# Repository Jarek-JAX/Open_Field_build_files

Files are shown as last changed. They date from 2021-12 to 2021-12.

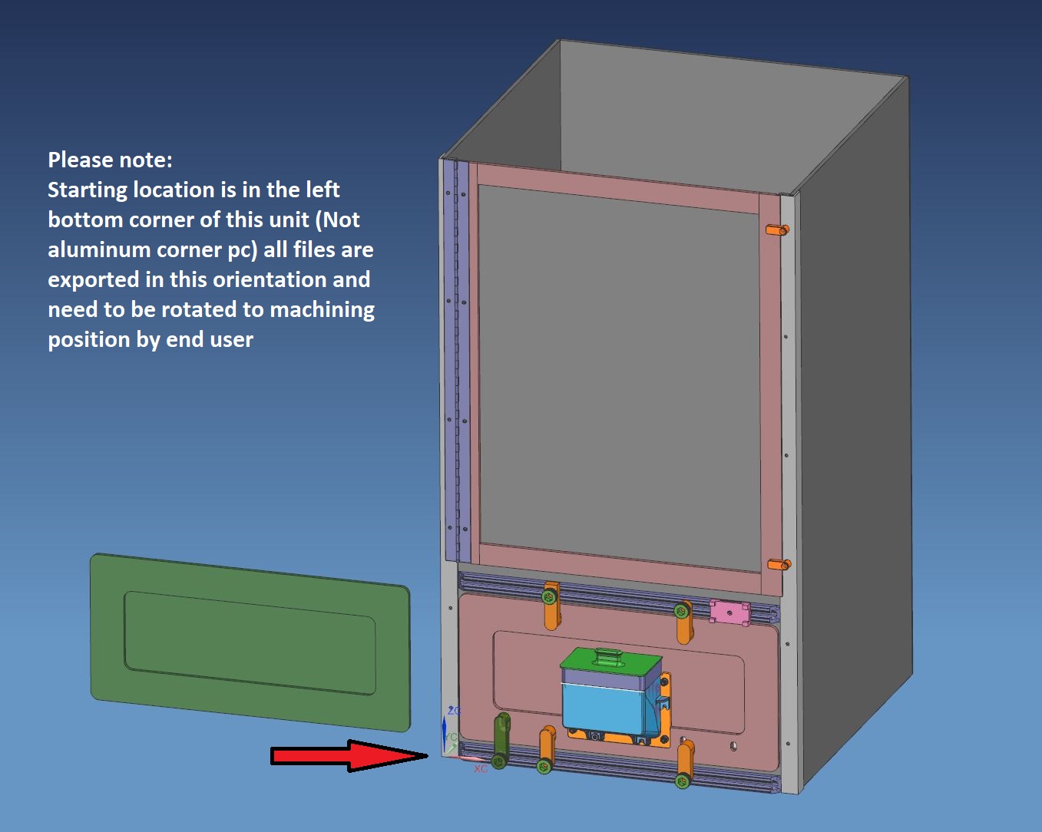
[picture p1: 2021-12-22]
02_Starting_location_and_orientation.JPG

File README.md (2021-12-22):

# Open_Field_build_files
All files listed and posted are created in US inch format and can be easily converted using FreeCad or similar open source CAD program.
All .step files are 3D CAD models needed to create CNC programs for cutting, and size verifications. Please follow Files list for quantities needed and Assembly instructions
Aluminum food grade is also shown as Drafting in pdf for outsourcing machining throug for eg. www.hubs.com

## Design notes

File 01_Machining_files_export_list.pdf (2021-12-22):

All Files are exported in .STEP203 Format | All Dimmensions are in US Inch

links:
Name | Material | Required
1 Floor | EXP PVC - White | 1 | *** EXP PVC White (https://www.curbellplastics.com/Shop-Materials/Product/Sintra-Expanded-PVC-Sheet/W01-06173/SINTRA-Expanded-PVC-Sheet-SINTRA-VERS-(formerly-e-pvc-)-Bright-Whit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)
2 Back_Wall | EXP PVC - Light Gray | 1
3 Side_Walls | EXP PVC - Light Gray | 2 | **** EXP PVC Light Gray (https://www.curbellplastics.com/Shop-Materials/Product/Sintra-Expanded-PVC-Sheet/W01-01036/SINTRA-Expanded-PVC-Sheet-SINTRA-Light-Gray-(6-mm-x-48-in-x-96-in)-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)
4 Front_Wall | EXP PVC - Light Gray | 1
5 Upper_Door | EXP PVC - Light Gray | 1 | Aluminum_Rail_Cut (https://www.mcmaster.com/47065T68-47065T681/)
6 Door_Frame_Long_1 | EXP PVC - Light Gray | 1
7 Door_Frame_Long_2 | EXP PVC - Light Gray | 1 | Derlin (https://www.mcmaster.com/8573K13/)
8 Door_Frame_Short | EXP PVC - Light Gray | 1
9 Front_Panel_Food_1 | EXP PVC - Light Gray | 1 | Aluminum_Corner (https://www.mcmaster.com/88805K77-88805K774/)
10 Front_Panel_Food_2 | EXP PVC - Light Gray | 1
11 Front_Panel_Blank_1 | EXP PVC - Light Gray | 1 | Piano_Hinge (https://www.mcmaster.com/1658A15-1658A4/)
12 Front_Panel_Blank_2 | EXP PVC - Light Gray | 1
13 Food_Grade | Aluminum | 1
14 Aluminum_Rail_Cut | Aluminum | 2
15 Light_ring_square | Derlin (Or simmilar) | 1
16 Aluminum_Corner | Aluminm | 2
17 Piano_Hinge | Stainless_Steel | 1

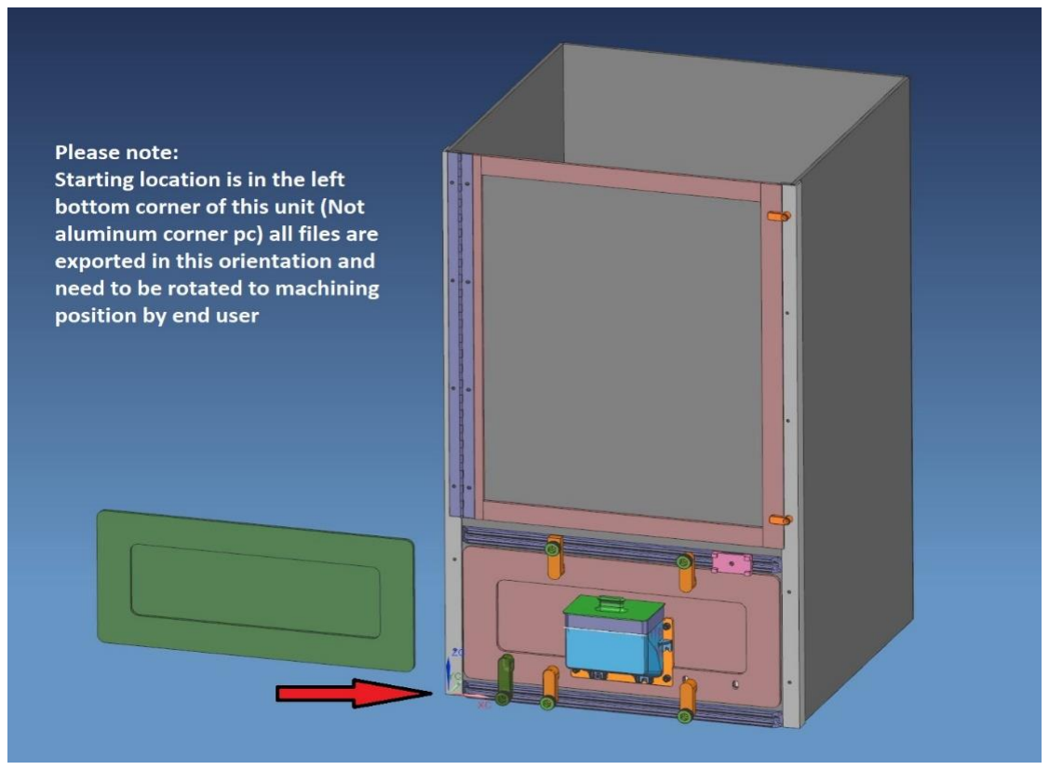
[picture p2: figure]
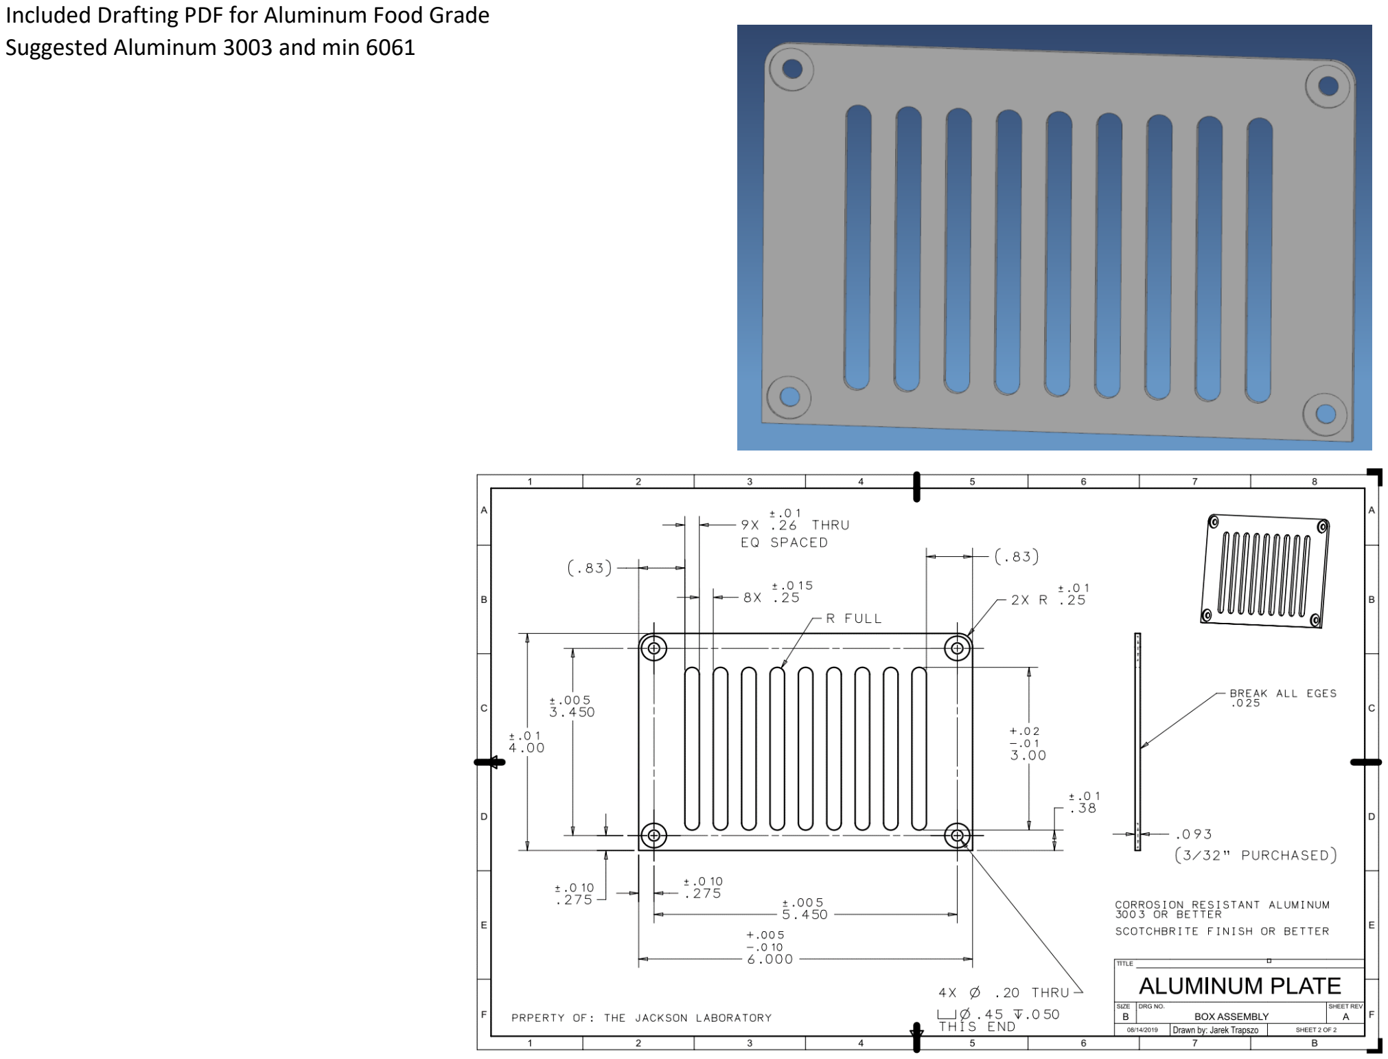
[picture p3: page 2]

Included Drafting PDF for Aluminum Food Grade Suggested Aluminum 3003 and min 6061

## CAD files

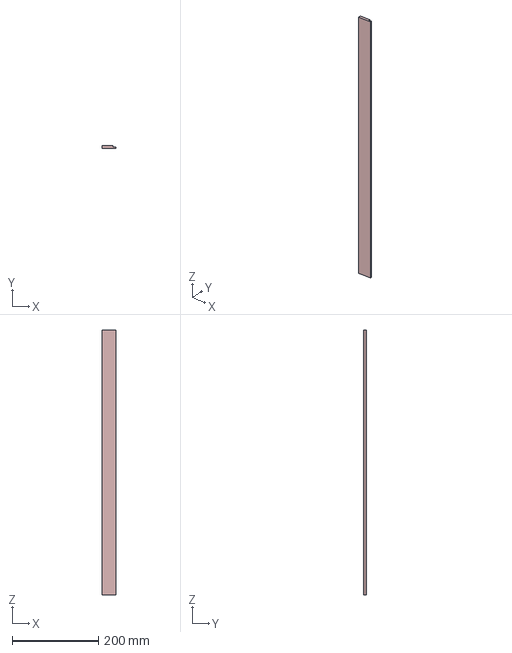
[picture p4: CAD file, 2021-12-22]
Door_frame_Long_1.stp
31.7 x 6.35 x 613.4 mm

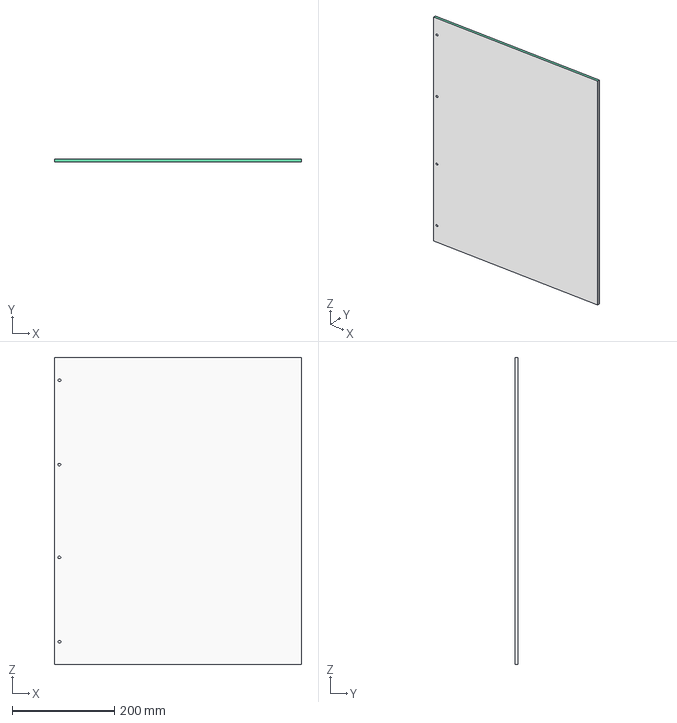
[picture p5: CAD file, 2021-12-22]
Upper_Door.stp
483.4 x 6.35 x 600.7 mm

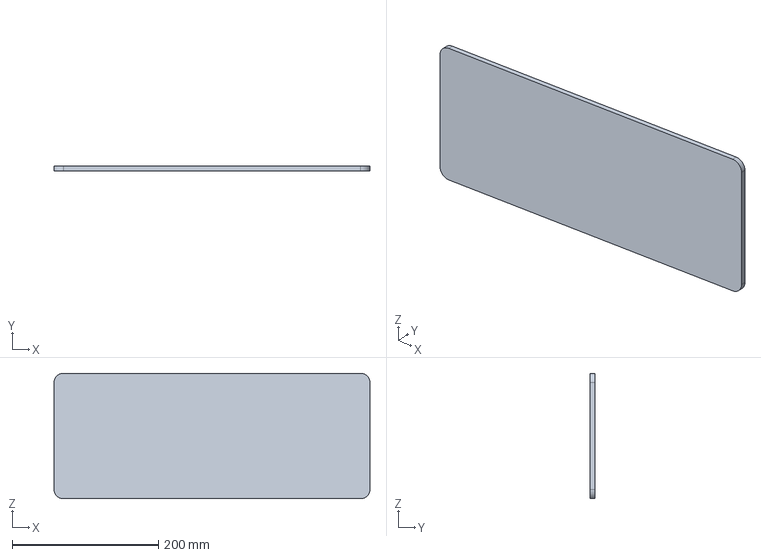
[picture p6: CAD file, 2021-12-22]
Front_Panel_Blank_1.stp
431.8 x 6.35 x 171.5 mm

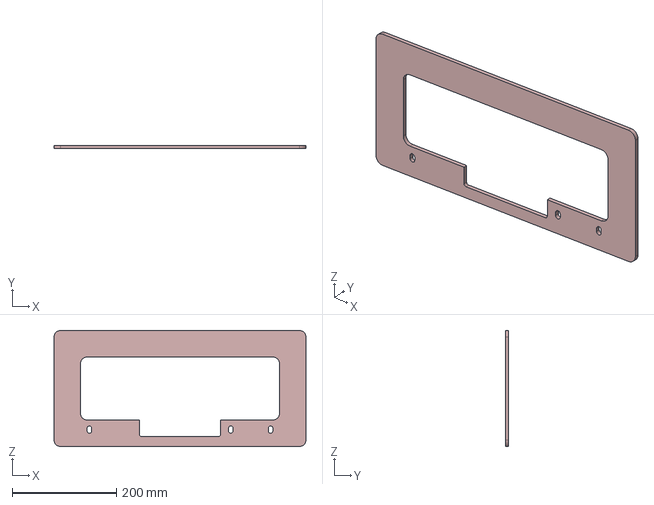
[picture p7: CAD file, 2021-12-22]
Front_Panel_Food_2.stp
482.6 x 6.35 x 222.2 mm

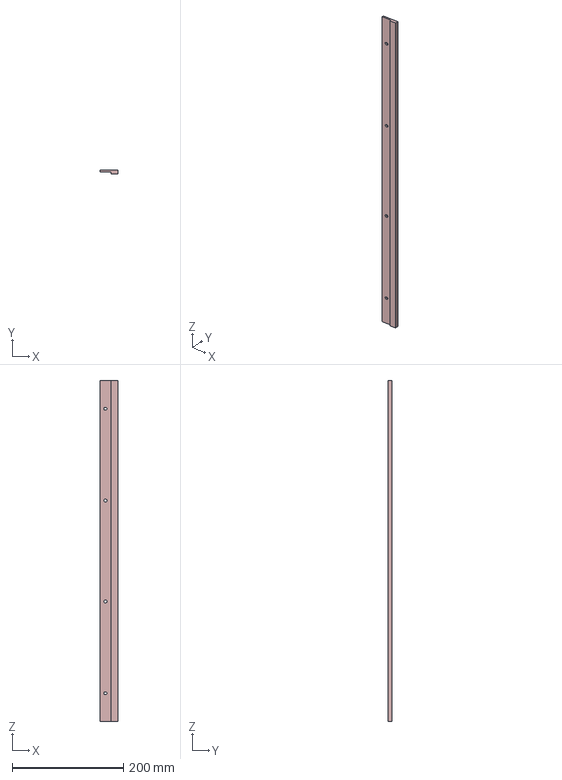
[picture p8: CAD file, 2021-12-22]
Door_frame_Long_2.stp
31.8 x 6.35 x 613.4 mm

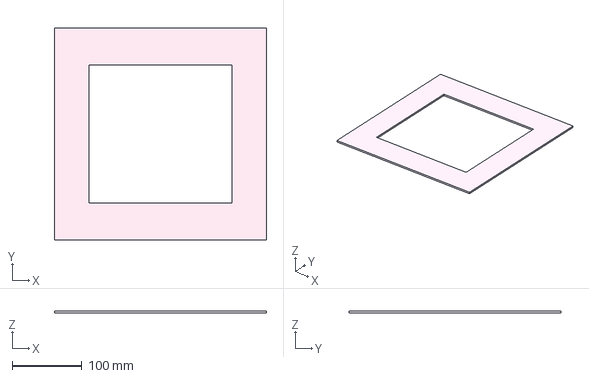
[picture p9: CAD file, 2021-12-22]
Light_ring_square.stp
304.8 x 304.8 x 3.18 mm

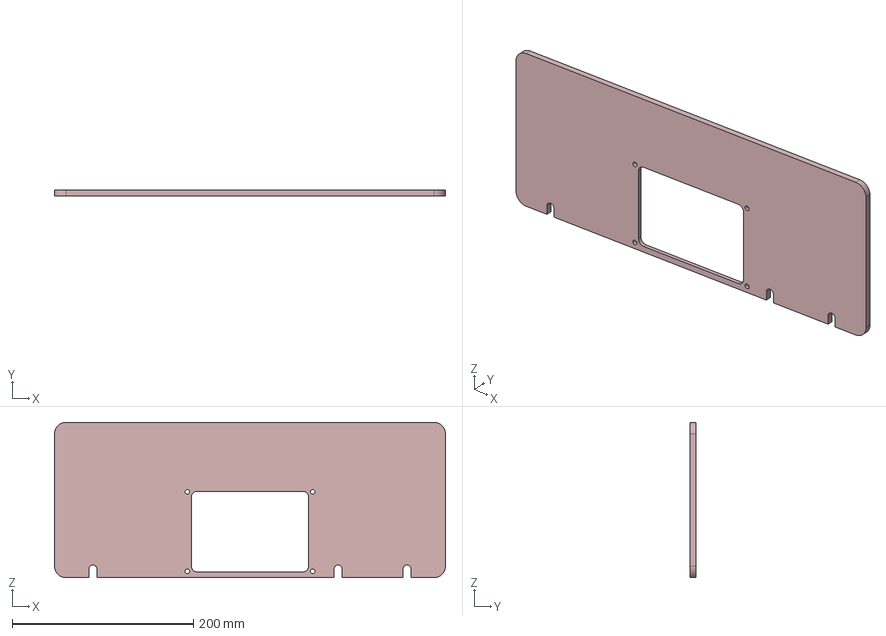
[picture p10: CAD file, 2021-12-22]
Front_Panel_Food_1.stp
431.8 x 6.35 x 171.5 mm

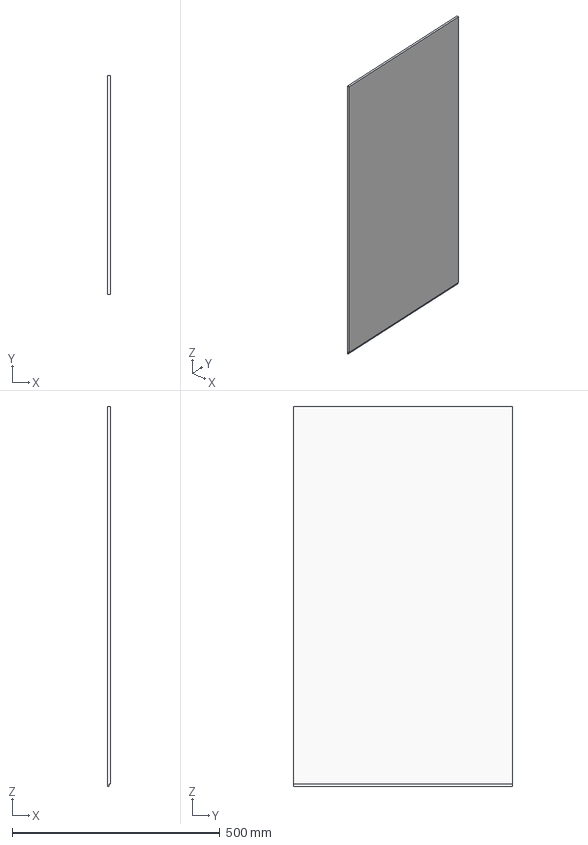
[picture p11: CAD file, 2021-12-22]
Side_Walls.stp
6.35 x 527.1 x 914.4 mm

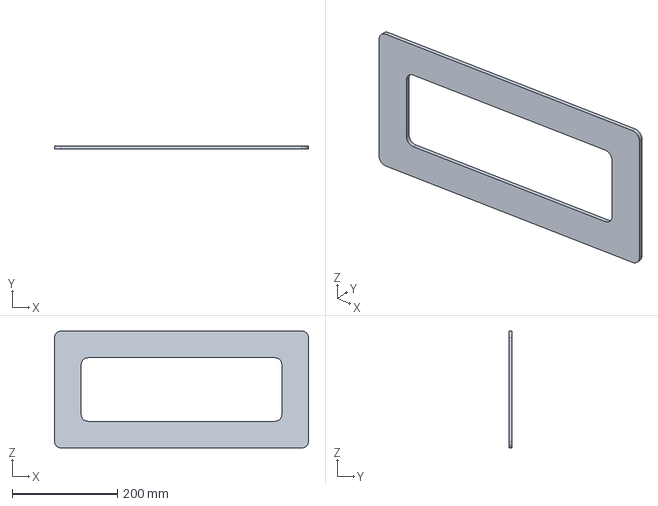
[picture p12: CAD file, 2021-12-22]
Front_Panel_Blank_2.stp
482.6 x 6.35 x 222.2 mm

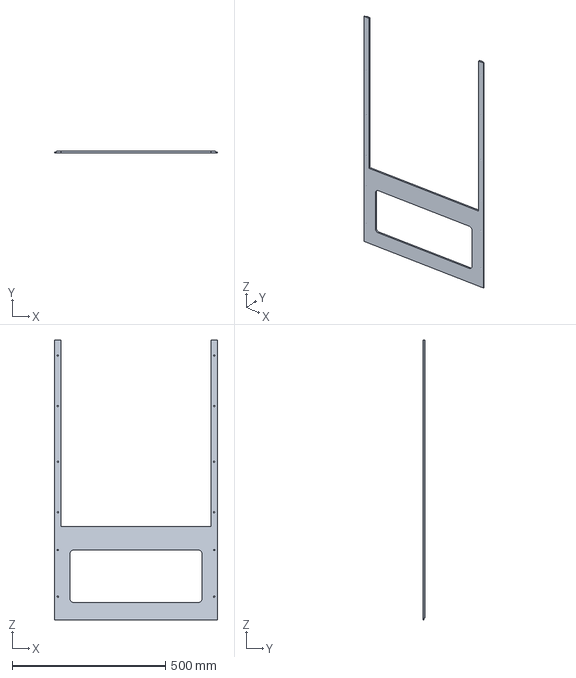
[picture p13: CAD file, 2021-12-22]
Front_wall.stp
533.4 x 6.35 x 914.4 mm

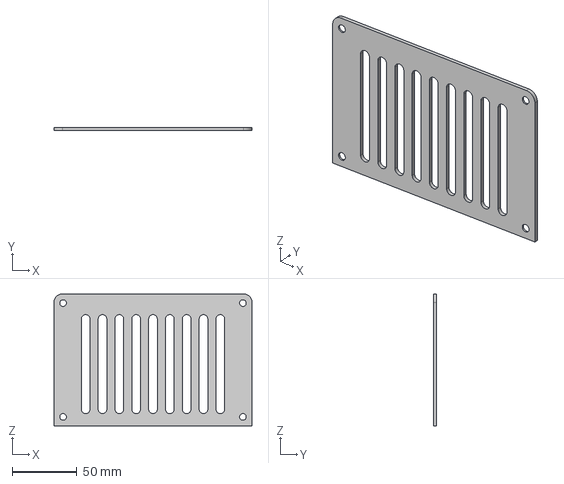
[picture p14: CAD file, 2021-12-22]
Food_Grade.stp
152.4 x 2.36 x 101.6 mm

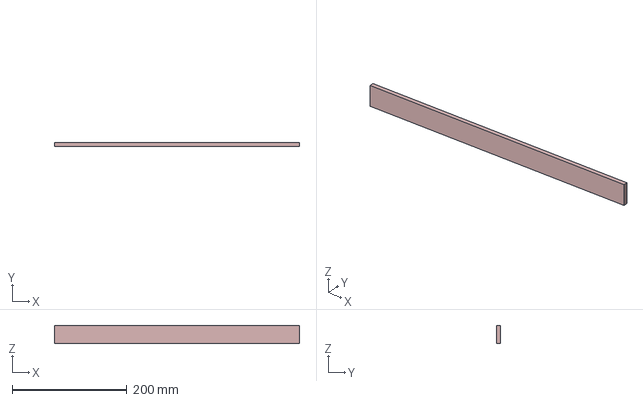
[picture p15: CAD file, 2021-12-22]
Door_frame_Short.stp
426.7 x 6.35 x 31.8 mm

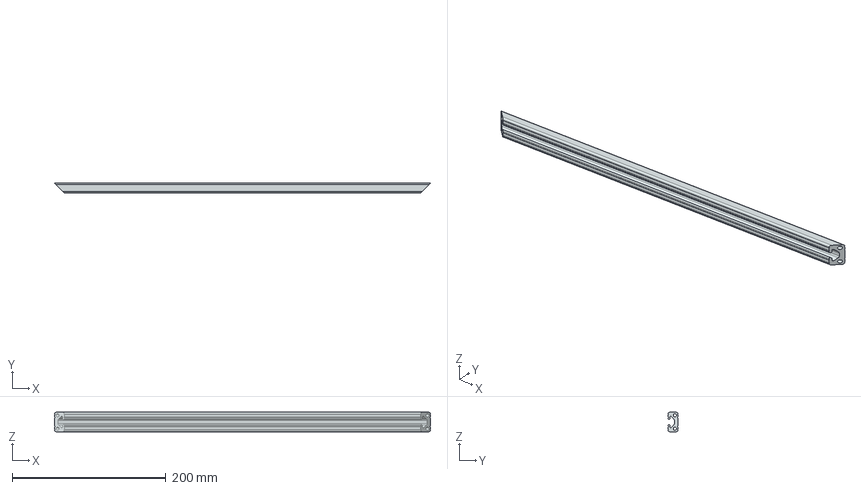
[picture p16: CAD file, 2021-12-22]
Alluminum_rail_cut.stp
488.7 x 12.7 x 25.4 mm

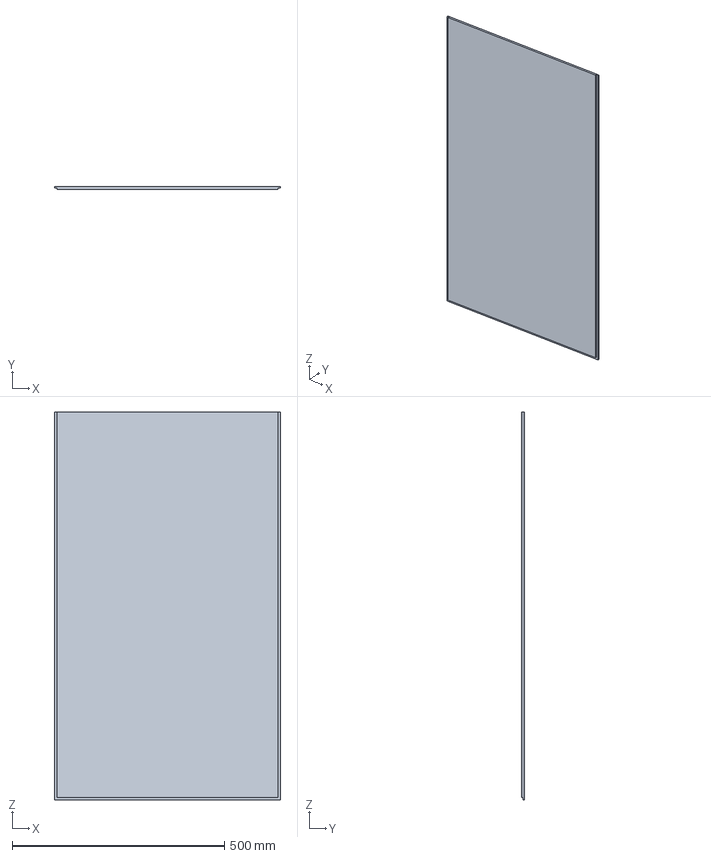
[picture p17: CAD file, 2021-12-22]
Back_Wall.stp
533.4 x 6.35 x 914.4 mm

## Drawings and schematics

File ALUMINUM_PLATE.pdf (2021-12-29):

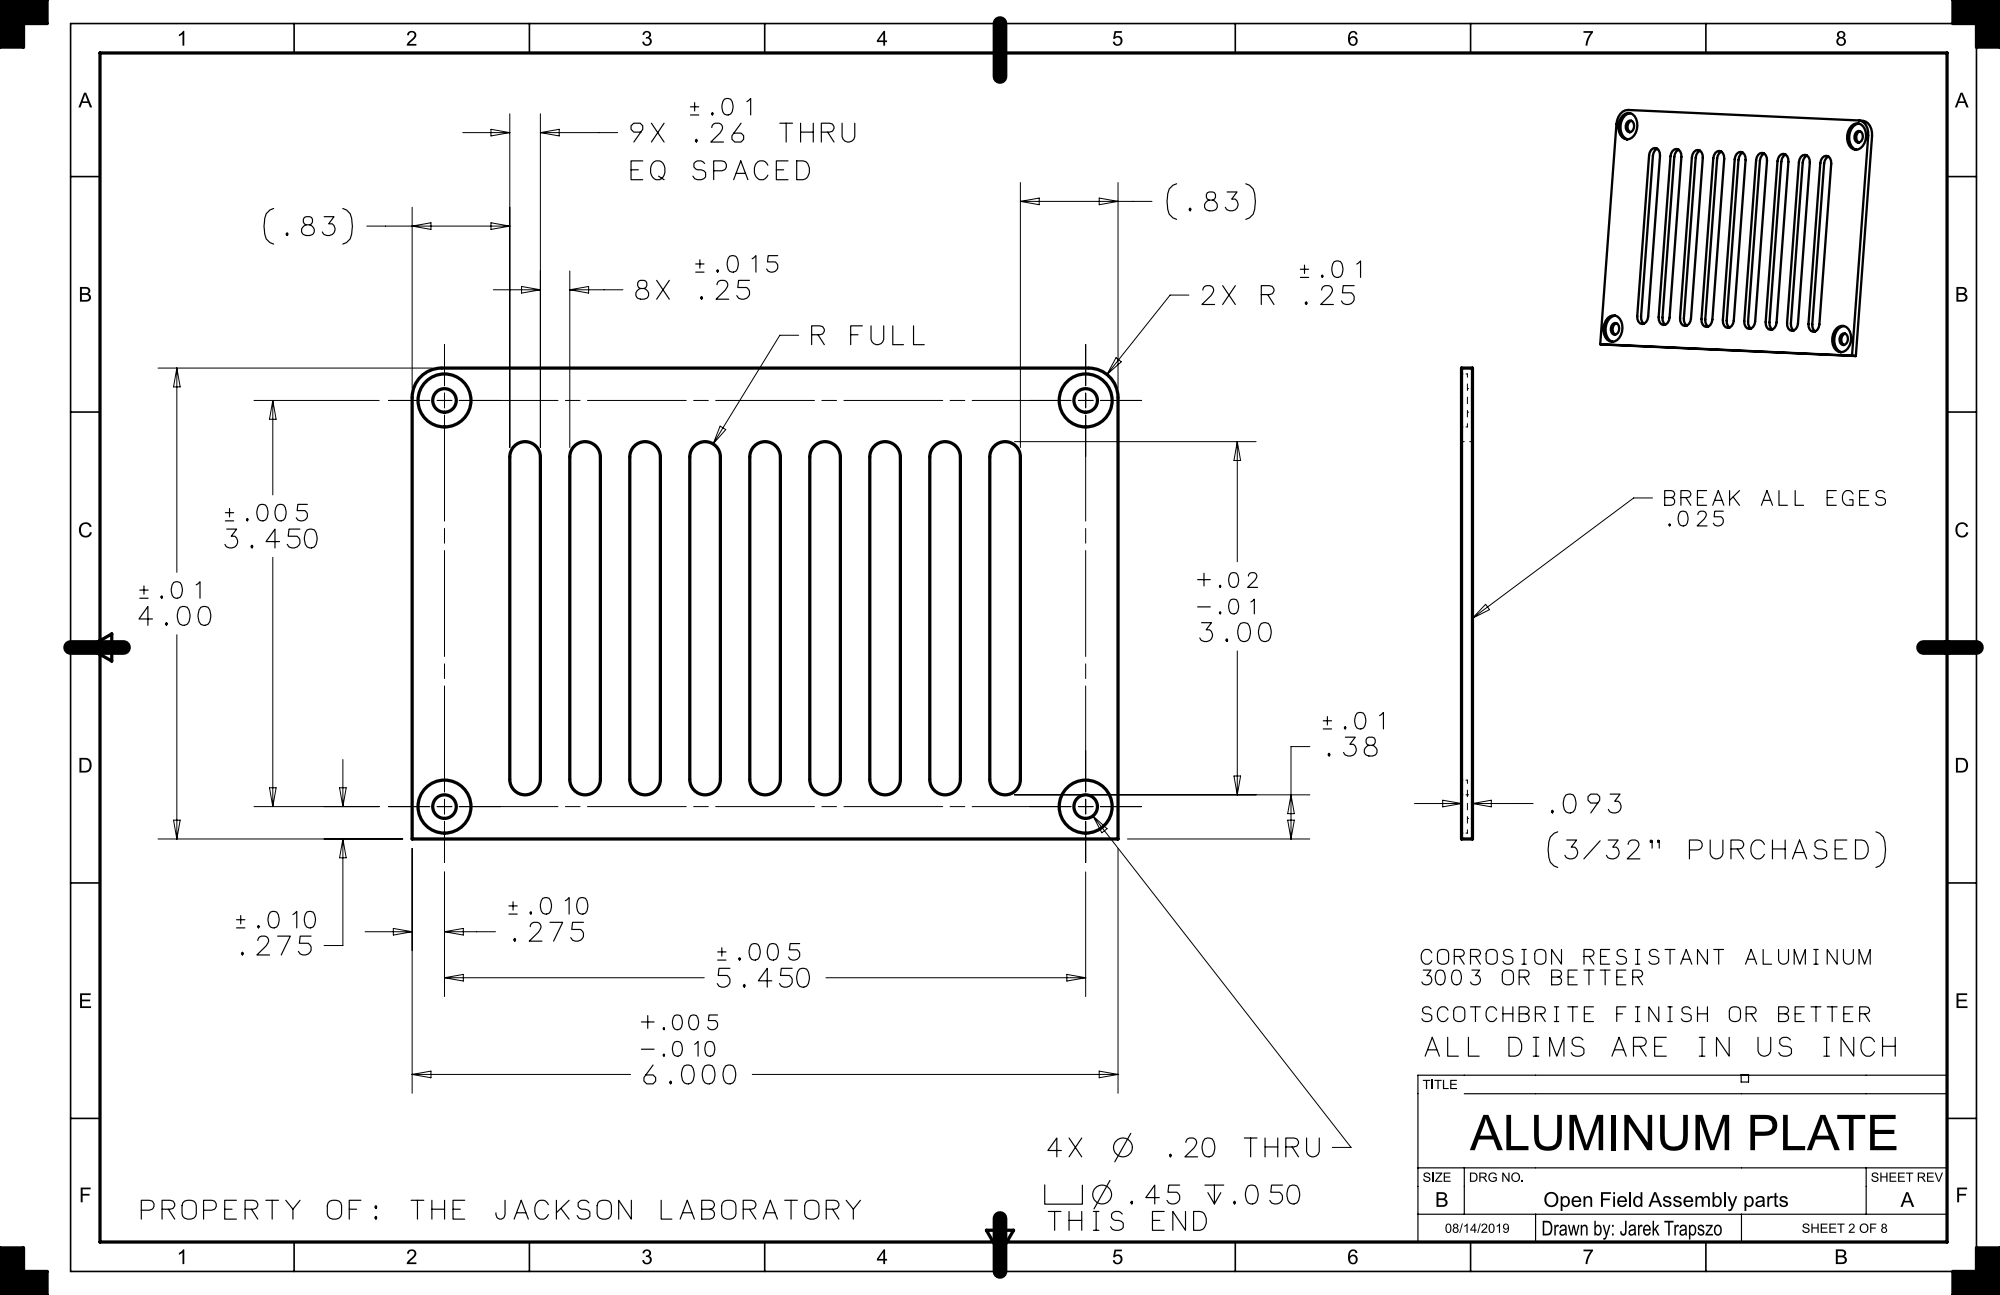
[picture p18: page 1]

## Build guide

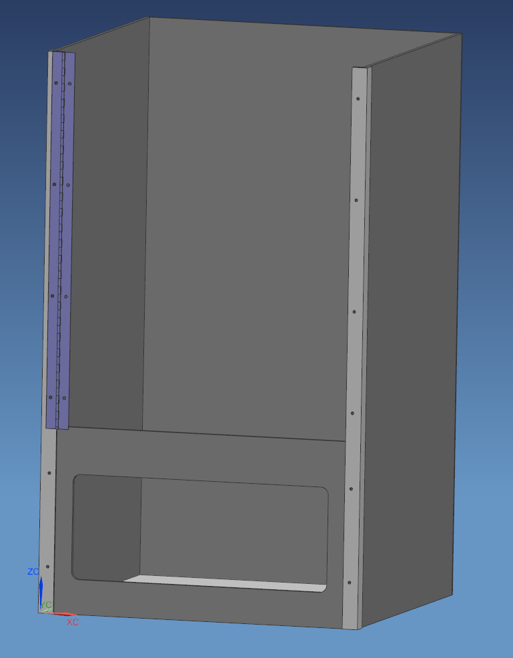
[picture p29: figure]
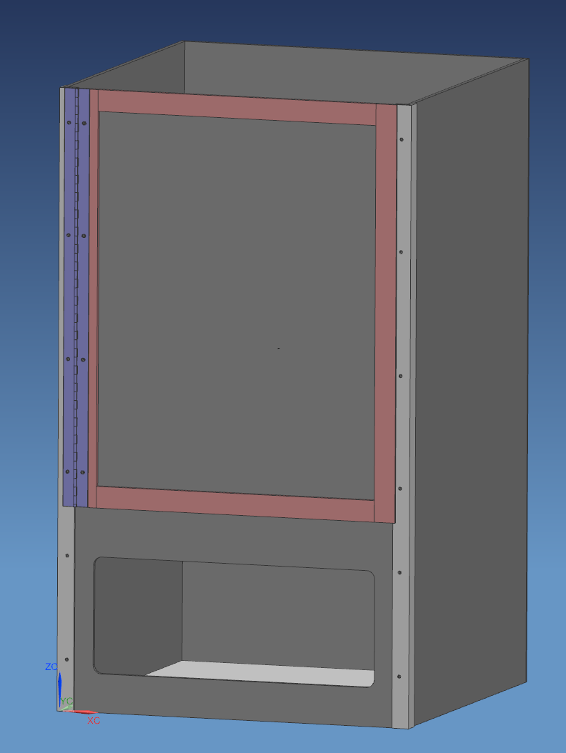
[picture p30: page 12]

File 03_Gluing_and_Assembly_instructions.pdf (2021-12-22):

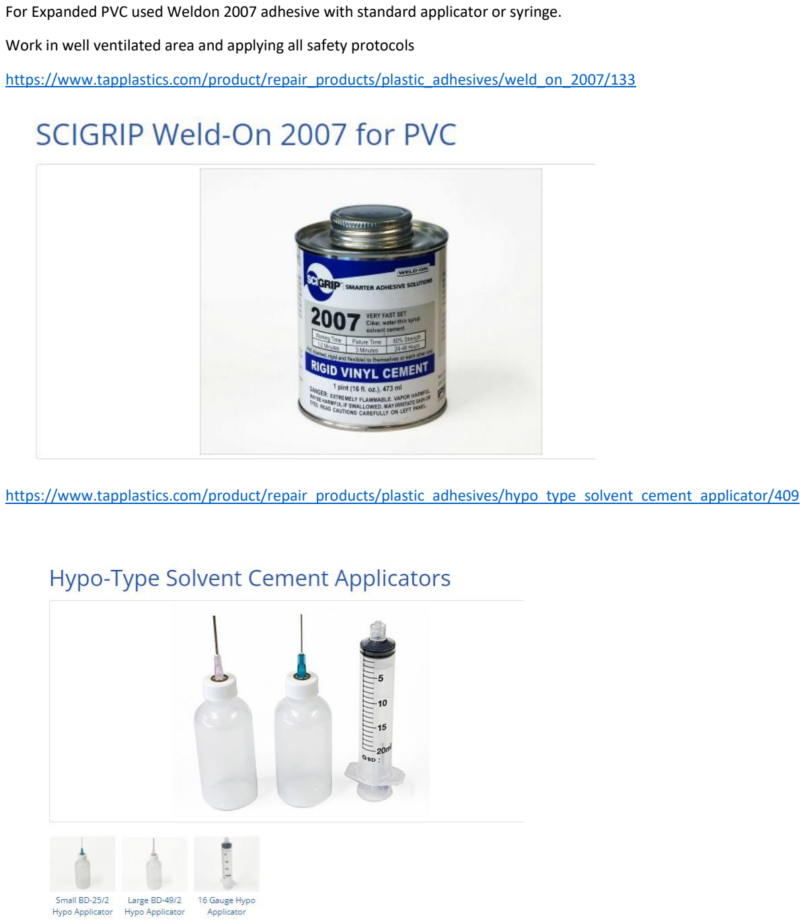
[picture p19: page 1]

For Expanded PVC used Weldon 2007 adhesive with standard applicator or syringe.

Work in well ventilated area and applying all safety protocols

https://www.tapplastics.com/product/repair_products/plastic_adhesives/weld_on_2007/133

https://www.tapplastics.com/product/repair_products/plastic_adhesives/hypo_type_solvent_cement_applicator/409

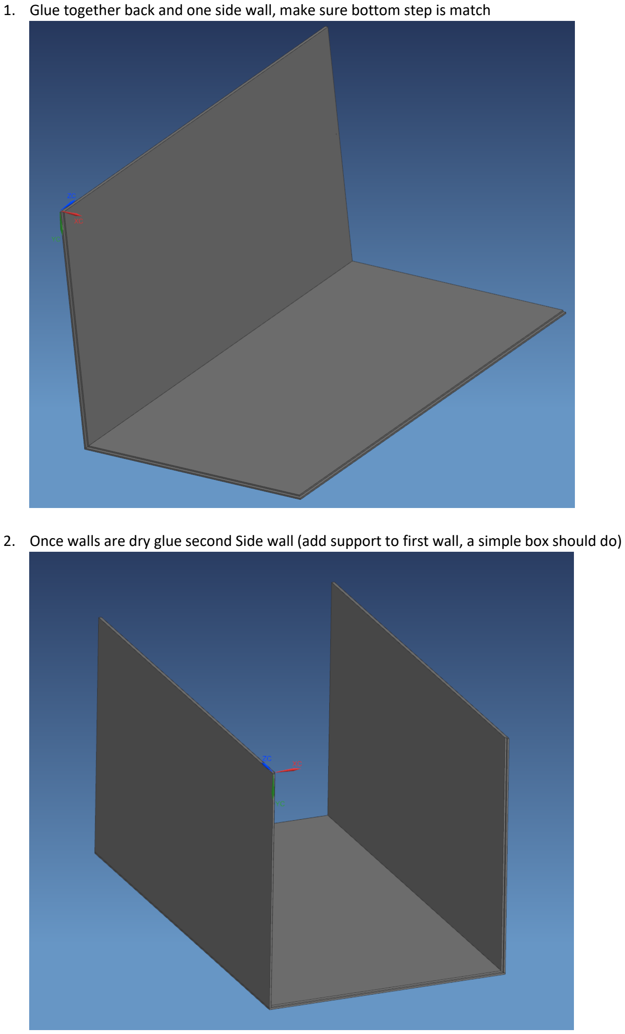
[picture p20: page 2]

1. Glue together back and one side wall, make sure bottom step is match
2. Once walls are dry glue second Side wall (add support to first wall, a simple box should do)

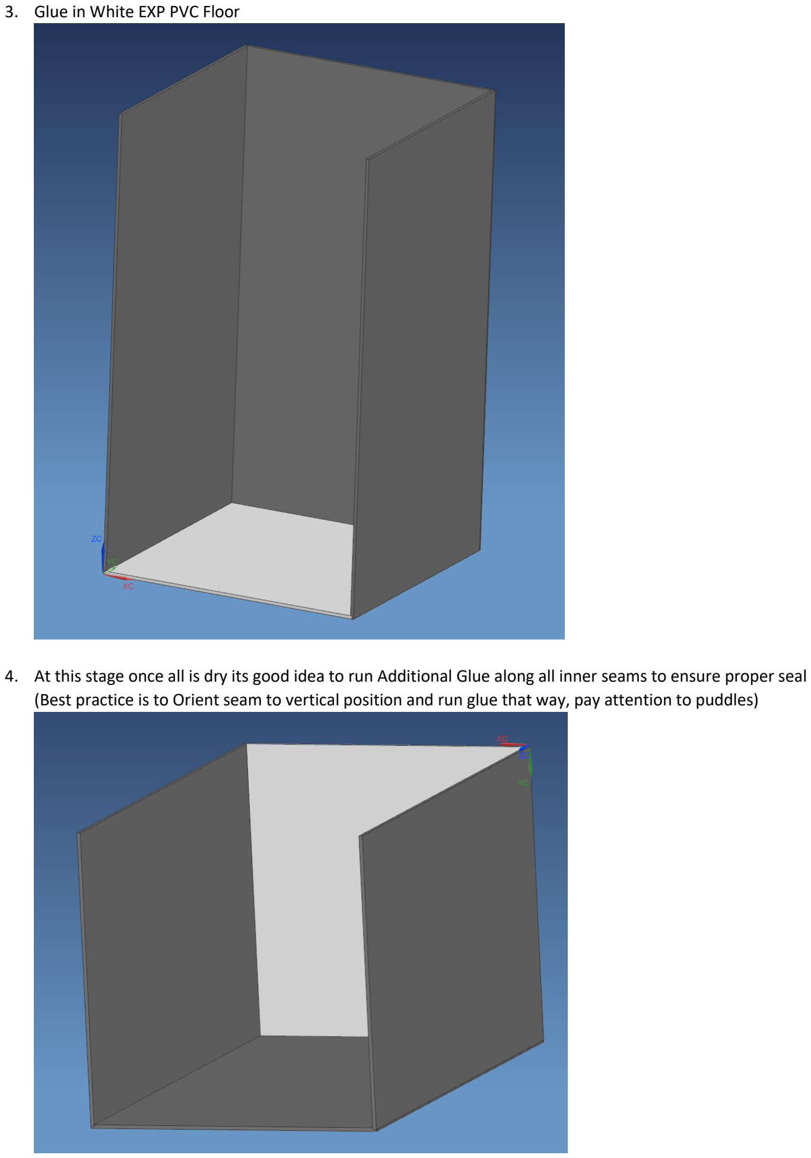
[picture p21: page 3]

3. Glue in White EXP PVC Floor
4. At this stage once all is dry its good idea to run Additional Glue along all inner seams to ensure proper seal (Best practice is to Orient seam to vertical position and run glue that way, pay attention to puddles)

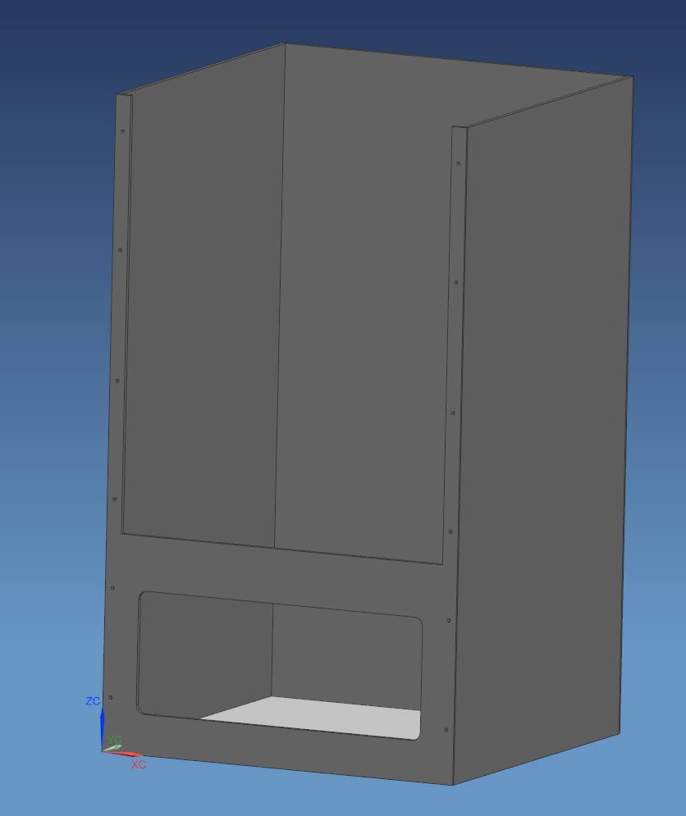
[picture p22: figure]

5. Glue in Front wall, make sure thin uprights are properly set in place

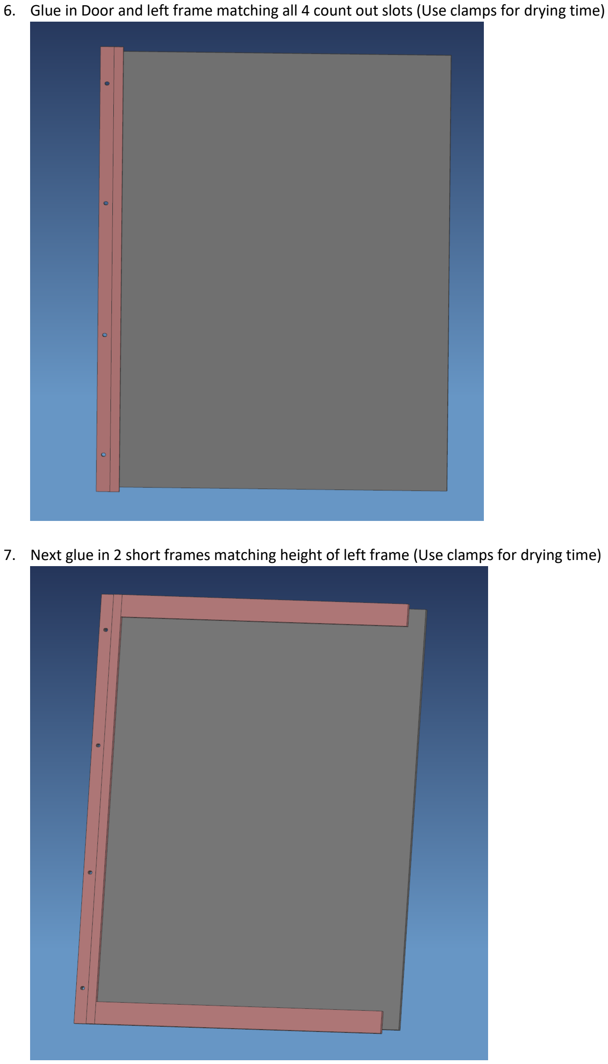
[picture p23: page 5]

6. Glue in Door and left frame matching all 4 count out slots (Use clamps for drying time)
7. Next glue in 2 short frames matching height of left frame (Use clamps for drying time)

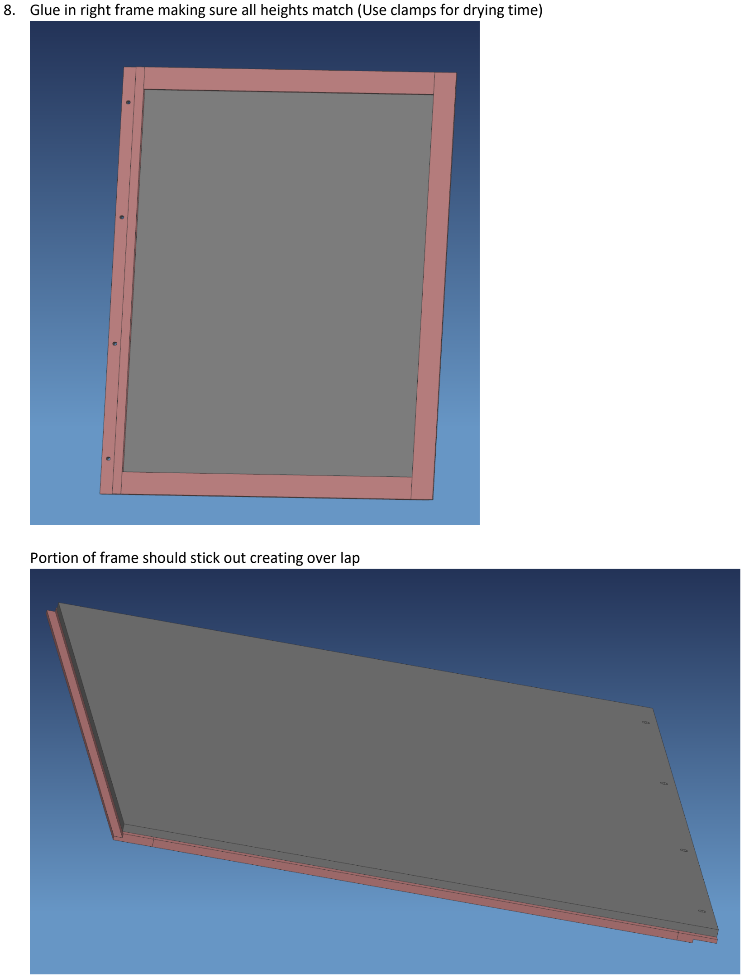
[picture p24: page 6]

8. Glue in right frame making sure all heights match (Use clamps for drying time)

Portion of frame should stick out creating over lap

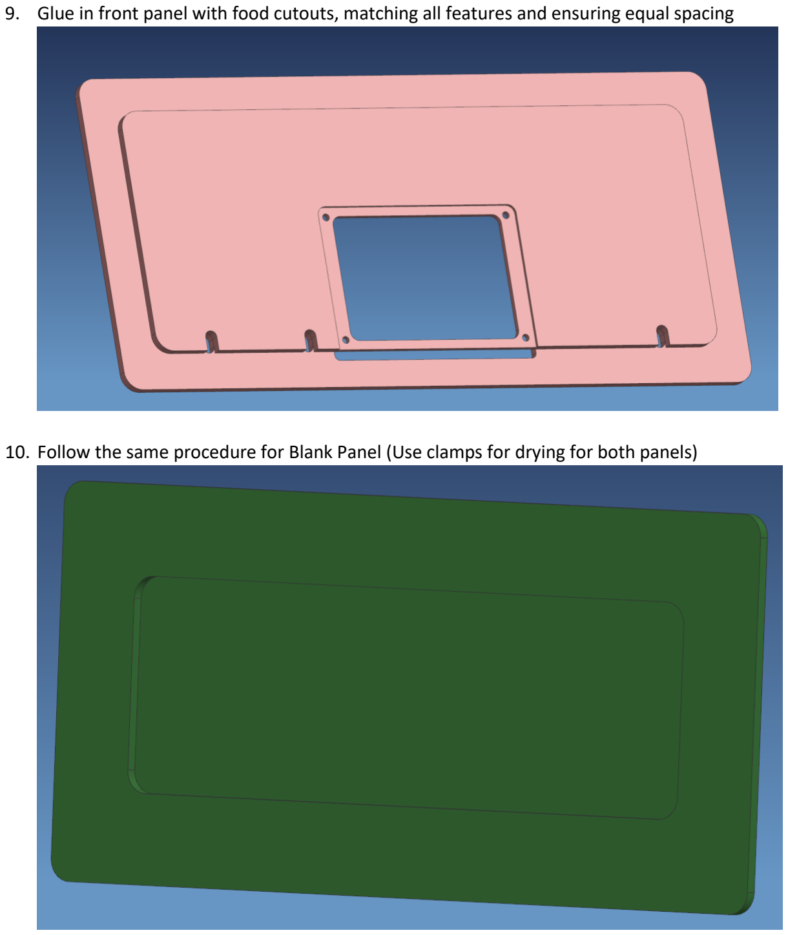
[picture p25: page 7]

9. Glue in front panel with food cutouts, matching all features and ensuring equal spacing
10. Follow the same procedure for Blank Panel (Use clamps for drying for both panels)

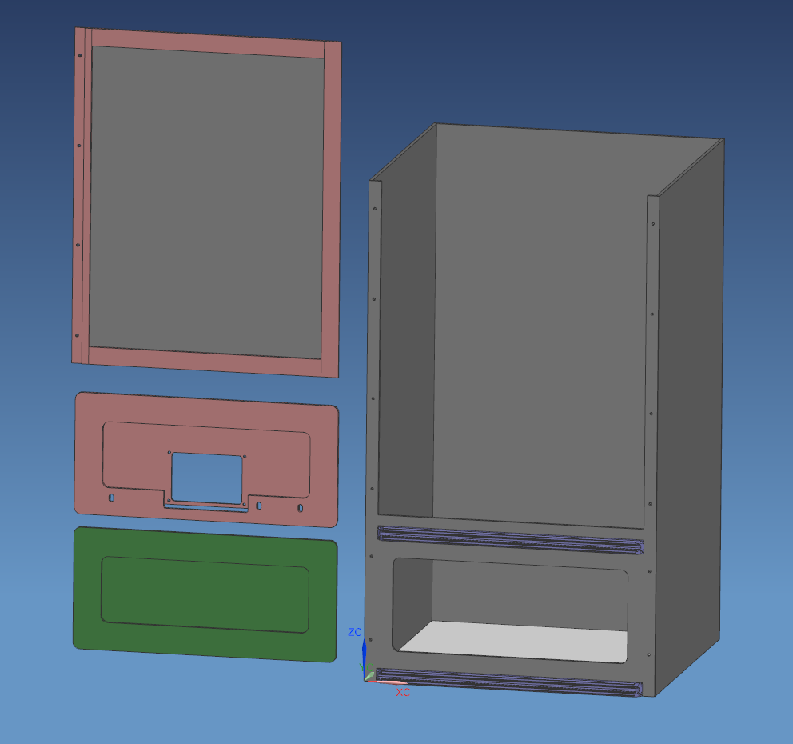
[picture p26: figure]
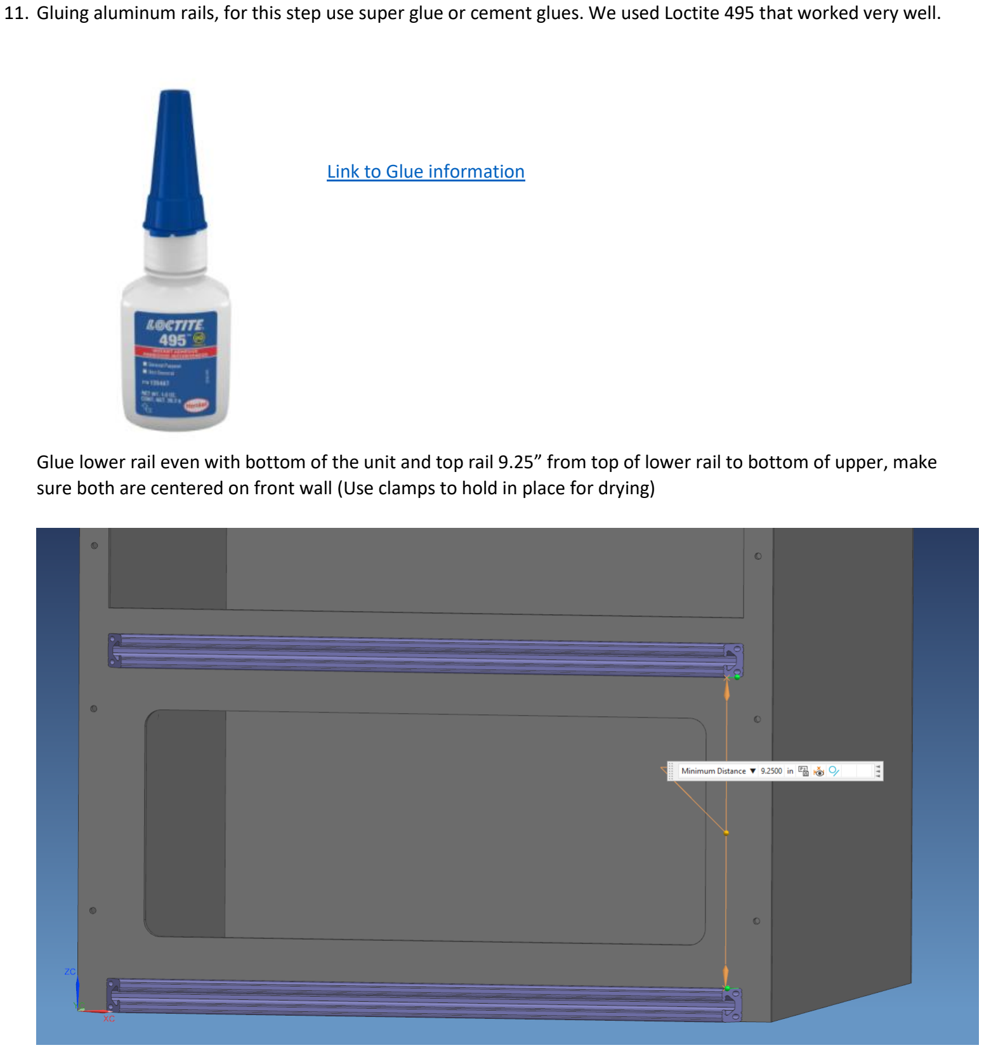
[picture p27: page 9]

11. Gluing aluminum rails, for this step use super glue or cement glues. We used Loctite 495 that worked very well.

Link to Glue information (https://www.henkel-adhesives.com/us/en/product/instant-adhesives/loctite_495.html)

Glue lower rail even with bottom of the unit and top rail 9.25” from top of lower rail to bottom of upper, make sure both are centered on front wall (Use clamps to hold in place for drying)

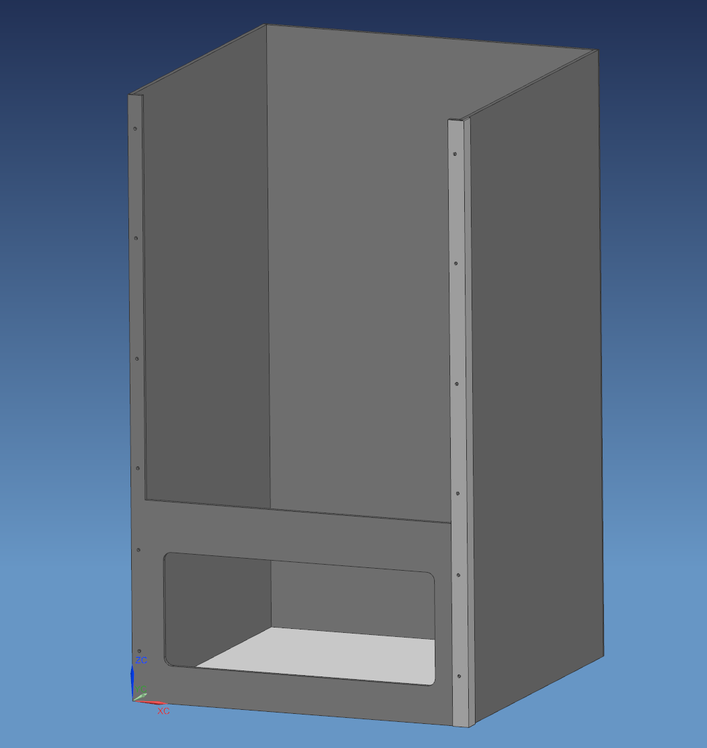
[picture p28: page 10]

12. Aluminum Corners – purpose of this part is to strengthen open frame doorway.
Make sure to purchase aluminum corners with straight inside corner.
Cut those to match unit’s height and mark all hole’s locations using machined front as template,
Drill all holes and fasten corners to the units 2 lower holes (Near opening) using #10-32 or #10-24 nylon screws and nuts, trim those flush when done.

13. Hinge: purchase stainless steel piano hinge from part list, it does not need to be with holes as only two will match per side. Cut Hinge to 24 1/8” (61.25 mm) and mark holes location from one of the uprights. Notice on door there 4 small slots so mark center of those for hinge drilling (this is for fine tuning door)
14. when ready attach hinge to either upright using same screws as for aluminum corners (this design allows left of right opening) and attach door the hinge, trim screws length even with nuts.
